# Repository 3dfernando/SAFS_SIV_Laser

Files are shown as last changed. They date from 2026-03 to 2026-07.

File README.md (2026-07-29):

# FSIV - A high-speed Focusing Schlieren Velocimetry system

Big thanks to MazinLab for publishing their laser driver! It enabled us to build this project at a very low cost!

## Samples

Here's a couple samples of the images acquired with this light source:

| Shear Layer of a M=0.98 jet (dt=800 ns) | Boundary Layer of a M=0.91 plug nozzle (dt=800 ns) |
|---|---|
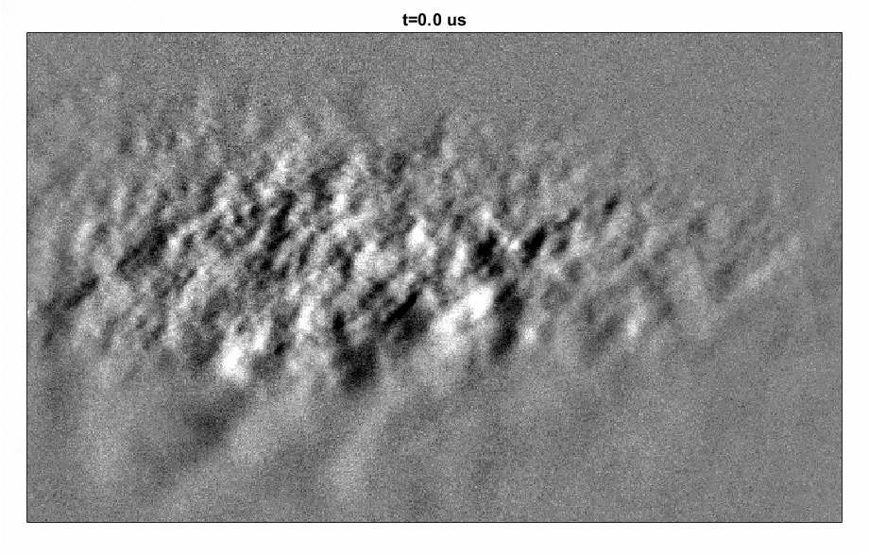
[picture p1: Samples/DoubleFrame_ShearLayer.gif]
Shear Layer
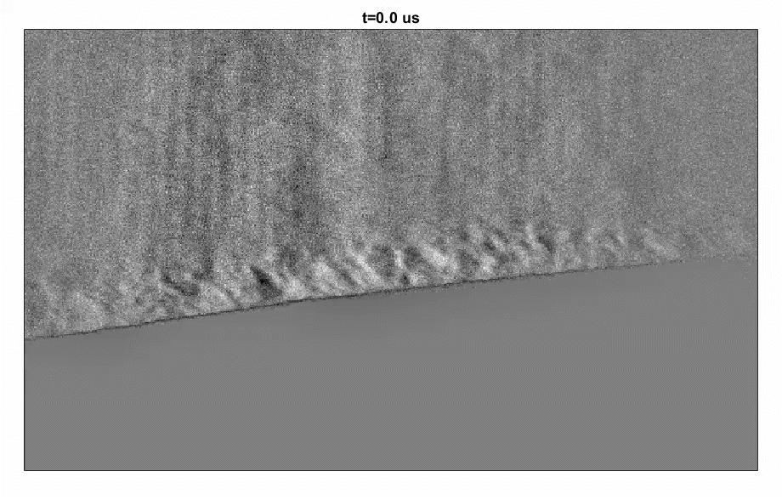
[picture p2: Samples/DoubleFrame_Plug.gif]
Boundary Layer
|  |  |

## Project Description

Velocimetry in high-speed aerodynamics (supersonic flows, more specifically) is very challenging. The flow velocities are so high that you need a high-frequency light source to be able to capture all the dynamics of the flow. More challengingly, the high velocities also bring the required delay between consecutive frames to order <500ns, requiring two light sources and the staggering of pulses.

For Particle Image Velocimetry (PIV), the laser must deliver sufficient pulse energy to scatter enough light onto the camera sensor — typically ≥10 mJ/pulse. Combined with the high-speed requirement, a suitable light source can exceed $200,000 USD, making this research prohibitively expensive even for well-funded laboratories. However, for schlieren imaging the amount of light required is much lower - about 10nJ/pulse are sufficient to fully illuminate the camera sensor and overcome the light losses. Thus, we developed a light source capable of ~400nJ/pulse and 30ns pulse width, which is adequate for most schlieren needs. 

Convective velocity — the velocity of turbulent structures and a key contributor to noise sources in aeroacoustics — requires at least two consecutive PIV velocity field measurements to be estimated from velocity data. However, if the flow structure can be captured directly through focusing schlieren (which images density gradients in the flow), it is possible to measure convective velocity directly by cross-correlating consecutive schlieren images.

Further, the double-pulsed schlieren images can also be processed with Online Dynamic Mode Decomposition (ODMD) to extract the coherent behavior of the flow at very high frequencies, limited by the Nyquist frequency based on the inter-frame pulse delay dt (typically <300 ns). For example, at dt=300 ns, this enables the observation of coherent structures up to ~1.7 MHz — beyond the capability of state-of-the-art high-speed cameras — at full camera resolution.

With our SAFS-SIV system, we are able to build a light source for under USD 1,000 capable of 50 kHz double-pulses with a 30 ns pulse width. At supersonic speeds, a 30 ns pulse corresponds to only ~2 μm of particle displacement, nearly eliminating motion blur. This low-cost device opens the door to high-speed flow diagnostics for a much broader range of research groups and institutions.

## Driver Picture

Below a photograph of our laser drivers forming a double-pulse system in a 1.0 mm fiber optic:

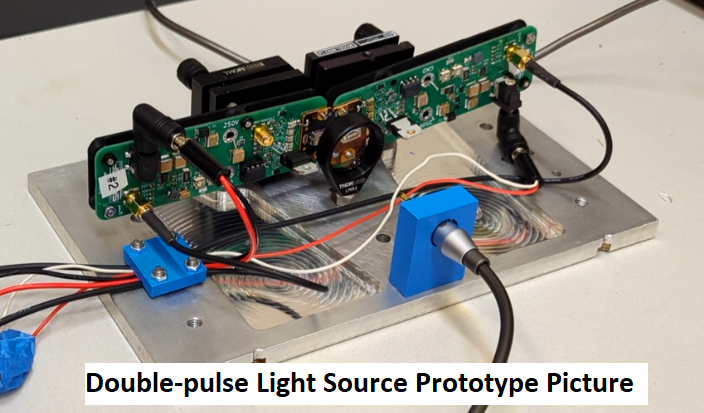
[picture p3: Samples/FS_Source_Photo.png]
Fiber source laser photo


A closer view of the PCB design:

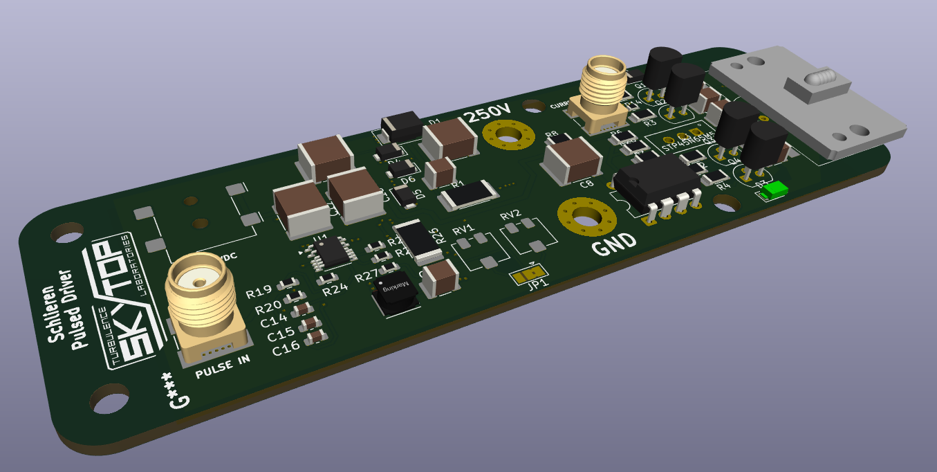
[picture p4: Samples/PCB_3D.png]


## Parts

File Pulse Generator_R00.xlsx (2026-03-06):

Description | Qty | Price/ea | Price total | Link
C2,C3,C4,C5,C6,C7 - 47p | 6 | $1.77 | $10.62 | https://www.digikey.com/en/products/detail/vishay-vitramon/VJ1210A470JXGAT5Z/1559967
SMA Connector | 3 | $6.95 | $20.85 | https://www.digikey.com/en/products/detail/amphenol-rf/132134-10/3125418
SMA/BNC Cable | 2 | $15.48 | $30.96 | https://www.digikey.com/en/products/detail/crystek-corporation/CCBNS-MM-RG174-18/1964572
C8,C12,C19 - 100n | 3 | $0.71 | $2.13 | https://www.digikey.com/en/products/detail/tdk-corporation/C4532X7R2J104K230KA/789694?s=N4IgTCBcDaICxwKwFowGYAMHkEZkDkARAHQBcQBdAXyA
C10,C18 - 1u | 2 | $2.85 | $5.70 | https://www.digikey.com/en/products/detail/kyocera-avx/2220CC105KAZ2A/11568650
C11,C16 - 1u | 2 | $0.08 | $0.16 | https://www.digikey.com/en/products/detail/samsung-electro-mechanics/CL10B105KP8NNNC/3887604?s=N4IgTCBcDaIIxgOwDYC0cCcAWNdUDkARAHQBcQBdAXyA
C15,C24 - 1n | 2 | $0.08 | $0.16 | https://www.digikey.com/en/products/detail/kemet/C0603C102K5RACTU/411081
C20,C21 - 220n | 2 | $1.00 | $2.00 | https://www.digikey.com/en/products/detail/murata-electronics/GRM55DR72J224KW01L/789368?s=N4IgTCBcDaICwE4AMBaAzAVjKgjCgcgCIA6ALiALoC%2BQA
C22,C23 - 2.2u | 2 | $0.18 | $0.36 | https://www.digikey.com/en/products/detail/murata-electronics/GRM188Z71E225ME43D/13905077
C1 - 10n | 1 | $0.38 | $0.38 | https://www.digikey.com/en/products/detail/johanson-dielectrics-inc/VPDF102W103K1GV001E/1557829
C14 - 220n | 1 | $0.15 | $0.15 | https://www.digikey.com/en/products/detail/murata-electronics/GCM188R71H224KA64D/2123158?s=N4IgTCBcDaICwE4AMBaArHJYUEYUDkARAHQBcQBdAXyA
C17 - 10u | 1 | $1.89 | $1.89 | https://www.digikey.com/en/products/detail/kyocera-avx/22201C106MAT2A/5431507
R2, R3, R4, R5, R6, R7 - 0Ohm | 6 | $0.10 | $0.60 | https://www.digikey.com/en/products/detail/stackpole-electronics-inc/RMCF1210ZT0R00/1715043
R8, R9, R10, R11, R12, R13 -0.5Ohm | 6 | $0.39 | $2.34 | https://www.digikey.com/en/products/detail/yageo/RL1210FR-070R5L/2827687
R14, R15, R19 - 50Ohm | 3 | $1.58 | $4.74 | https://www.digikey.com/en/products/detail/vishay-dale-thin-film/FC0603E50R0BTBST1/1769753
R18, R20 - 10k | 2 | $0.10 | $0.20 | https://www.digikey.com/en/products/detail/stackpole-electronics-inc/RMCF0603JT10K0/1758104
R1 - 1.2k | 1 | $0.15 | $0.15 | https://www.digikey.com/en/products/detail/koa-speer-electronics-inc/RK73B2ETTD122J/10314990
R16 - 4.7k | 1 | $0.10 | $0.10 | https://www.digikey.com/en/products/detail/yageo/RC0603FR-074K7L/727212
R21 - 18.2k | 1 | $0.10 | $0.10 | https://www.digikey.com/en/products/detail/stackpole-electronics-inc/RMCF0603FT18K2/1761004
R22 - 6.04k | 1 | $0.10 | $0.10 | https://www.digikey.com/en/products/detail/koa-speer-electronics-inc/RK73H1JTTD6041F/9844956
R23 - 107k | 1 | $0.10 | $0.10 | https://www.digikey.com/en/products/detail/yageo/RC0603FR-07107KL/726895
R24 - 84.5k | 1 | $0.10 | $0.10 | https://www.digikey.com/en/products/detail/yageo/RC0603FR-0784K5L/727408
R25 - 1M | 1 | $0.11 | $0.11 | https://www.digikey.com/en/products/detail/koa-speer-electronics-inc/RN73H1JTTD1004B25/10675094
R26 - 20Ohm | 1 | $0.10 | $0.10 | https://www.digikey.com/en/products/detail/stackpole-electronics-inc/RNCF0805DTE20R0/1708199
L1 - 10u | 1 | $2.35 | $2.35 | https://www.digikey.com/en/products/detail/w%C3%BCrth-elektronik/74437324100/2791051?s=N4IgTCBcDaIOwGYwFoFoGzIIzIHIBEAdAFxAF0BfIA
D2, D3, D4, D5, D6 - DFLS1150 | 5 | $0.38 | $1.90 | https://www.digikey.com/en/products/detail/diodes-incorporated/DFLS1150Q-7/6110470
D1 - S3MB-13F | 1 | $0.40 | $0.40 | https://www.digikey.com/en/products/detail/diodes-incorporated/S3MB-13-F/755456
U1 - LT8365 | 1 | $7.69 | $7.69 | https://www.digikey.com/en/products/detail/analog-devices-inc/LT8365EMSE-TRPBF/11586903
U2 - ISO6740 | 1 | $2.55 | $2.55 | https://www.digikey.com/en/products/detail/texas-instruments/ISO6740QDWRQ1/15205178
U3 - ADP7142ARDZ-5.0 | 1 | $4.89 | $4.89 | https://www.digikey.com/en/products/detail/analog-devices-inc/ADP7142ARDZ-5-0/6566216
U4 - LR8K4-G | 1 | $1.26 | $1.26 | https://www.digikey.com/en/products/detail/microchip-technology/LR8K4-G/4902849
RV1 - 50k | 1 | $1.58 | $1.58 | https://www.digikey.com/en/products/detail/bourns-inc/3314J-1-503E/86658
RV1 - 10k | 1 | $1.58 | $1.58 | https://www.digikey.com/en/products/detail/bourns-inc/3314J-1-103E/86580
J2 - Jack 2.0x5.5mm | 1 | $1.80 | $1.80 | https://www.digikey.com/en/products/detail/w%C3%BCrth-elektronik/694106106102/5047822?s=N4IgTCBcDaIOwGYwFoCsBOM7kEZkDkARAHQBcQBdAXyA
PLPT5 447KA Diode | 1 | $29.07 | $29.07 | https://www.digikey.com/en/products/detail/ams-osram-usa-inc/PLPT5-447KA/13541196
Nichita NUBM44 | 1 | $84.95 | $84.95 | https://www.amazon.com/Nichia-NUBM44-NUBM47-450nm-Laser/dp/B07662NHZZ
Diode Housing | 1 | $7.88 | $7.88 | https://www.amazon.com/12x30mm-9-0mm-Laser-Housing-200-1100nm/dp/B01G6GMIEM
Grand Total |  |  | $232.00

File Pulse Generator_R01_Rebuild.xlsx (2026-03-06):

Description | Qty | Price/ea | Price total | Link
C2,C3,C4,C5,C6,C7 - 47p | 6 | $1.77 | $10.62 | https://www.digikey.com/en/products/detail/vishay-vitramon/VJ1210A470JXGAT5Z/1559967
IC1 - UCC24742p | 10 | $1.62 | $16.20 | https://www.digikey.com/en/products/detail/texas-instruments/UCC27424P/603254?s=N4IgTCBcDaIKoGEFgOwBYxoAogLoF8g
Q5 - STP45N65M5 | 4 | $8.53 | $34.12 | https://www.digikey.com/en/products/detail/stmicroelectronics/STP45N65M5/3088028?s=N4IgTCBcDaIMoBUAKAWArAOQGxoLJpAF0BfIA
C16 - 1u | 2 | $0.08 | $0.16 | https://www.digikey.com/en/products/detail/samsung-electro-mechanics/CL10B105KP8NNNC/3887604?s=N4IgTCBcDaIIxgOwDYC0cCcAWNdUDkARAHQBcQBdAXyA
R25 - 1M | 2 | $0.11 | $0.22 | https://www.digikey.com/en/products/detail/koa-speer-electronics-inc/RN73H1JTTD1004B25/10675094
R24 - 84.5k | 2 | $0.10 | $0.20 | https://www.digikey.com/en/products/detail/yageo/RC0603FR-0784K5L/727408
R27 - 5.1k | 2 | $0.10 | $0.20 | https://www.digikey.com/en/products/detail/stackpole-electronics-inc/RMCF0603FT5K10/1760908
R23 - 107k | 2 | $0.10 | $0.20 | https://www.digikey.com/en/products/detail/yageo/RC0603FR-07107KL/726895
RV1 - 50k | 2 | $1.58 | $3.16 | https://www.digikey.com/en/products/detail/bourns-inc/3314J-1-503E/86658
RV1 - 10k | 2 | $1.58 | $3.16 | https://www.digikey.com/en/products/detail/bourns-inc/3314J-1-103E/86580
C15 - 1n | 2 | $0.08 | $0.16 | https://www.digikey.com/en/products/detail/kemet/C0603C102K5RACTU/411081
C19 - 100n | 2 | $0.71 | $1.42 | https://www.digikey.com/en/products/detail/tdk-corporation/C4532X7R2J104K230KA/789694?s=N4IgTCBcDaICxwKwFowGYAMHkEZkDkARAHQBcQBdAXyA
C18 - 1u | 2 | $2.85 | $5.70 | https://www.digikey.com/en/products/detail/kyocera-avx/2220CC105KAZ2A/11568650
C8, C17 - 10u | 4 | $1.89 | $7.56 | https://www.digikey.com/en/products/detail/kyocera-avx/22201C106MAT2A/5431507
C20,C21 - 220n | 4 | $1.00 | $4.00 | https://www.digikey.com/en/products/detail/murata-electronics/GRM55DR72J224KW01L/789368?s=N4IgTCBcDaICwE4AMBaAzAVjKgjCgcgCIA6ALiALoC%2BQA
C14 - 220n | 2 | $0.15 | $0.30 | https://www.digikey.com/en/products/detail/murata-electronics/GCM188R71H224KA64D/2123158?s=N4IgTCBcDaICwE4AMBaArHJYUEYUDkARAHQBcQBdAXyA
LD1 - NUBB-45 | 2 | $129.00 | $258.00 | https://lasertree.com/products/nichia-nubb45-455nm-34w-blue-laser-diode
C1 - 10n | 2 | $0.38 | $0.76 | https://www.digikey.com/en/products/detail/johanson-dielectrics-inc/VPDF102W103K1GV001E/1557829
L1 - 10u | 2 | $2.35 | $4.70 | https://www.digikey.com/en/products/detail/w%C3%BCrth-elektronik/74437324100/2791051?s=N4IgTCBcDaIOwGYwFoFoGzIIzIHIBEAdAFxAF0BfIA
R14, R19 - 50 Ohm | 2 | $1.58 | $3.16 | https://www.digikey.com/en/products/detail/vishay-dale-thin-film/FC0603E50R0BTBST1/1769753
D2, D3, D4, D5, D6 - DFLS1150 | 10 | $0.38 | $3.80 | https://www.digikey.com/en/products/detail/diodes-incorporated/DFLS1150Q-7/6110470
R5, R6, R7, R28- 4.7 Ohm | 8 | $0.10 | $0.80 | https://www.digikey.com/en/products/detail/stackpole-electronics-inc/RMCF1206FT4R70/1759916
R1 - 1.2k | 2 | $0.76 | $1.52 | https://www.digikey.com/en/products/detail/te-connectivity-passive-product/35221K2JT/5245016
R26 - 20 Ohm | 2 | $1.14 | $2.28 | https://www.digikey.com/en/products/detail/te-connectivity-passive-product/352220RFT/5245035
R8 - 470 Ohm | 2 | $0.10 | $0.20 | https://www.digikey.com/en/products/detail/yageo/RC1210FR-07470RL/5919610
R2, R3, R4, R12 - 0.4 Ohm | 8 | $0.15 | $1.20 | https://www.digikey.com/en/products/detail/yageo/RL1206JR-070R4L/5925149
R20 - 10k | 2 | $0.10 | $0.20 | https://www.digikey.com/en/products/detail/stackpole-electronics-inc/RMCF0603JT10K0/1758104
D1 - S3MB-13F | 2 | $0.40 | $0.80 | https://www.digikey.com/en/products/detail/diodes-incorporated/S3MB-13-F/755456
Q1, Q2, Q3, Q4 - ZTX415 | 10 | $13.60 | $136.00 | https://www.digikey.com/en/products/detail/diodes-incorporated/ZTX415/190185?s=N4IgTCBcDaIFoBUAaAWAjAVgLQDkAiIAugL5A
1mm Multimode Fiber POF Patch Cords , 2.0m | 1 | $33.57 | $33.57 | https://i-fiberoptics.com/patchcord-detail.php?summaryrow=12&series=181L&stock_number=IF%20181L-2-0
Grand Total |  |  | $534.37

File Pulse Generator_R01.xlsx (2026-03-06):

Description | Qty | Price/ea | Price total | Link
C2,C3,C4,C5,C6,C7 - 47p | 6 | $1.77 | $10.62 | https://www.digikey.com/en/products/detail/vishay-vitramon/VJ1210A470JXGAT5Z/1559967
SMA Connector | 2 | $6.95 | $13.90 | https://www.digikey.com/en/products/detail/amphenol-rf/132134-10/3125418
SMA/BNC Cable | 2 | $15.48 | $30.96 | https://www.digikey.com/en/products/detail/crystek-corporation/CCBNS-MM-RG174-18/1964572
IC1 - UCC24742p | 1 | $1.62 | $1.62 | https://www.digikey.com/en/products/detail/texas-instruments/UCC27424P/603254?s=N4IgTCBcDaIKoGEFgOwBYxoAogLoF8g
Q5 - STP45N65M5 | 1 | $8.53 | $8.53 | https://www.digikey.com/en/products/detail/stmicroelectronics/STP45N65M5/3088028?s=N4IgTCBcDaIMoBUAKAWArAOQGxoLJpAF0BfIA
C16 - 1u | 1 | $0.08 | $0.08 | https://www.digikey.com/en/products/detail/samsung-electro-mechanics/CL10B105KP8NNNC/3887604?s=N4IgTCBcDaIIxgOwDYC0cCcAWNdUDkARAHQBcQBdAXyA
R25 - 1M | 1 | $0.11 | $0.11 | https://www.digikey.com/en/products/detail/koa-speer-electronics-inc/RN73H1JTTD1004B25/10675094
R24 - 84.5k | 1 | $0.10 | $0.10 | https://www.digikey.com/en/products/detail/yageo/RC0603FR-0784K5L/727408
R27 - 5.1k | 1 | $0.10 | $0.10 | https://www.digikey.com/en/products/detail/stackpole-electronics-inc/RMCF0603FT5K10/1760908
R23 - 107k | 1 | $0.10 | $0.10 | https://www.digikey.com/en/products/detail/yageo/RC0603FR-07107KL/726895
RV1 - 50k | 1 | $1.58 | $1.58 | https://www.digikey.com/en/products/detail/bourns-inc/3314J-1-503E/86658
RV1 - 10k | 1 | $1.58 | $1.58 | https://www.digikey.com/en/products/detail/bourns-inc/3314J-1-103E/86580
C15 - 1n | 1 | $0.08 | $0.08 | https://www.digikey.com/en/products/detail/kemet/C0603C102K5RACTU/411081
C19 - 100n | 1 | $0.71 | $0.71 | https://www.digikey.com/en/products/detail/tdk-corporation/C4532X7R2J104K230KA/789694?s=N4IgTCBcDaICxwKwFowGYAMHkEZkDkARAHQBcQBdAXyA
C18 - 1u | 1 | $2.85 | $2.85 | https://www.digikey.com/en/products/detail/kyocera-avx/2220CC105KAZ2A/11568650
C8, C17 - 10u | 2 | $1.89 | $3.78 | https://www.digikey.com/en/products/detail/kyocera-avx/22201C106MAT2A/5431507
C20,C21 - 220n | 2 | $1.00 | $2.00 | https://www.digikey.com/en/products/detail/murata-electronics/GRM55DR72J224KW01L/789368?s=N4IgTCBcDaICwE4AMBaAzAVjKgjCgcgCIA6ALiALoC%2BQA
C14 - 220n | 1 | $0.15 | $0.15 | https://www.digikey.com/en/products/detail/murata-electronics/GCM188R71H224KA64D/2123158?s=N4IgTCBcDaICwE4AMBaArHJYUEYUDkARAHQBcQBdAXyA
U1 - LT8365 | 1 | $7.69 | $7.69 | https://www.digikey.com/en/products/detail/analog-devices-inc/LT8365EMSE-TRPBF/11586903
LD1 - NUBM-44 | 1 | $24.95 | $24.95 | https://barnettunlimited.com/product/nubm44u/
C1 - 10n | 1 | $0.38 | $0.38 | https://www.digikey.com/en/products/detail/johanson-dielectrics-inc/VPDF102W103K1GV001E/1557829
L1 - 10u | 1 | $2.35 | $2.35 | https://www.digikey.com/en/products/detail/w%C3%BCrth-elektronik/74437324100/2791051?s=N4IgTCBcDaIOwGYwFoFoGzIIzIHIBEAdAFxAF0BfIA
J2 - Jack 2.0x5.5mm | 1 | $1.80 | $1.80 | https://www.digikey.com/en/products/detail/w%C3%BCrth-elektronik/694106106102/5047822?s=N4IgTCBcDaIOwGYwFoCsBOM7kEZkDkARAHQBcQBdAXyA
R14, R19 - 50 Ohm | 2 | $1.58 | $3.16 | https://www.digikey.com/en/products/detail/vishay-dale-thin-film/FC0603E50R0BTBST1/1769753
D2, D3, D4, D5, D6 - DFLS1150 | 5 | $0.38 | $1.90 | https://www.digikey.com/en/products/detail/diodes-incorporated/DFLS1150Q-7/6110470
R5, R6, R7, R28- 4.7 Ohm | 4 | $0.10 | $0.40 | https://www.digikey.com/en/products/detail/stackpole-electronics-inc/RMCF1206FT4R70/1759916
R1 - 1.2k | 1 | $0.76 | $0.76 | https://www.digikey.com/en/products/detail/te-connectivity-passive-product/35221K2JT/5245016
R26 - 20 Ohm | 1 | $1.14 | $1.14 | https://www.digikey.com/en/products/detail/te-connectivity-passive-product/352220RFT/5245035
R8 - 470 Ohm | 1 | $0.10 | $0.10 | https://www.digikey.com/en/products/detail/yageo/RC1210FR-07470RL/5919610
R2, R3, R4, R12 - 0.4 Ohm | 4 | $0.15 | $0.60 | https://www.digikey.com/en/products/detail/yageo/RL1206JR-070R4L/5925149
R20 - 10k | 1 | $0.10 | $0.10 | https://www.digikey.com/en/products/detail/stackpole-electronics-inc/RMCF0603JT10K0/1758104
D1 - S3MB-13F | 1 | $0.40 | $0.40 | https://www.digikey.com/en/products/detail/diodes-incorporated/S3MB-13-F/755456
Q1, Q2, Q3, Q4 - ZTX415 | 4 | $13.60 | $54.40 | https://www.digikey.com/en/products/detail/diodes-incorporated/ZTX415/190185?s=N4IgTCBcDaIFoBUAaAWAjAVgLQDkAiIAugL5A
Grand Total |  |  | $178.98

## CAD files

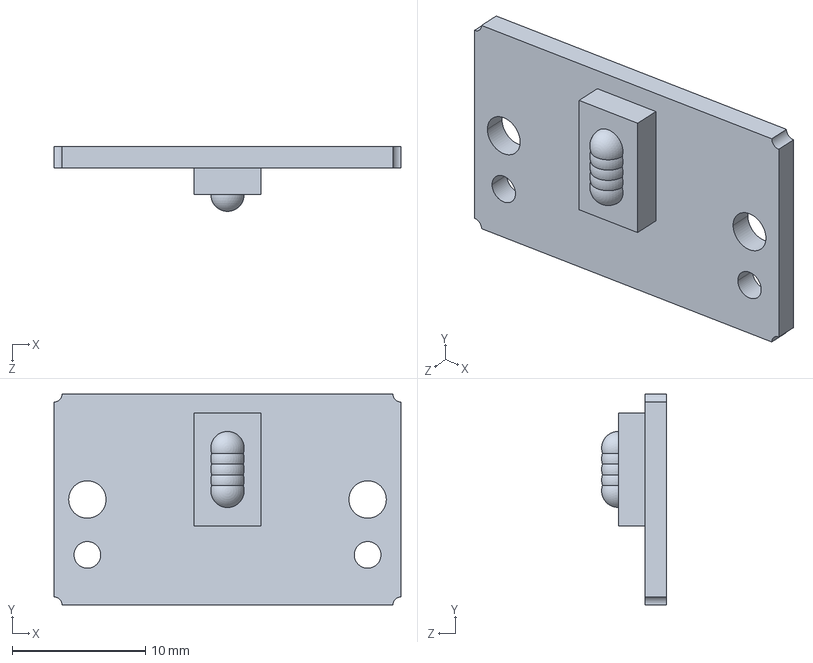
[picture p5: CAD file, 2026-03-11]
Laser_Driver/NUBB-45.STEP
26.0 x 15.8 x 4.86 mm

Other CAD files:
Laser_Driver/NUBB-45.SLDPRT

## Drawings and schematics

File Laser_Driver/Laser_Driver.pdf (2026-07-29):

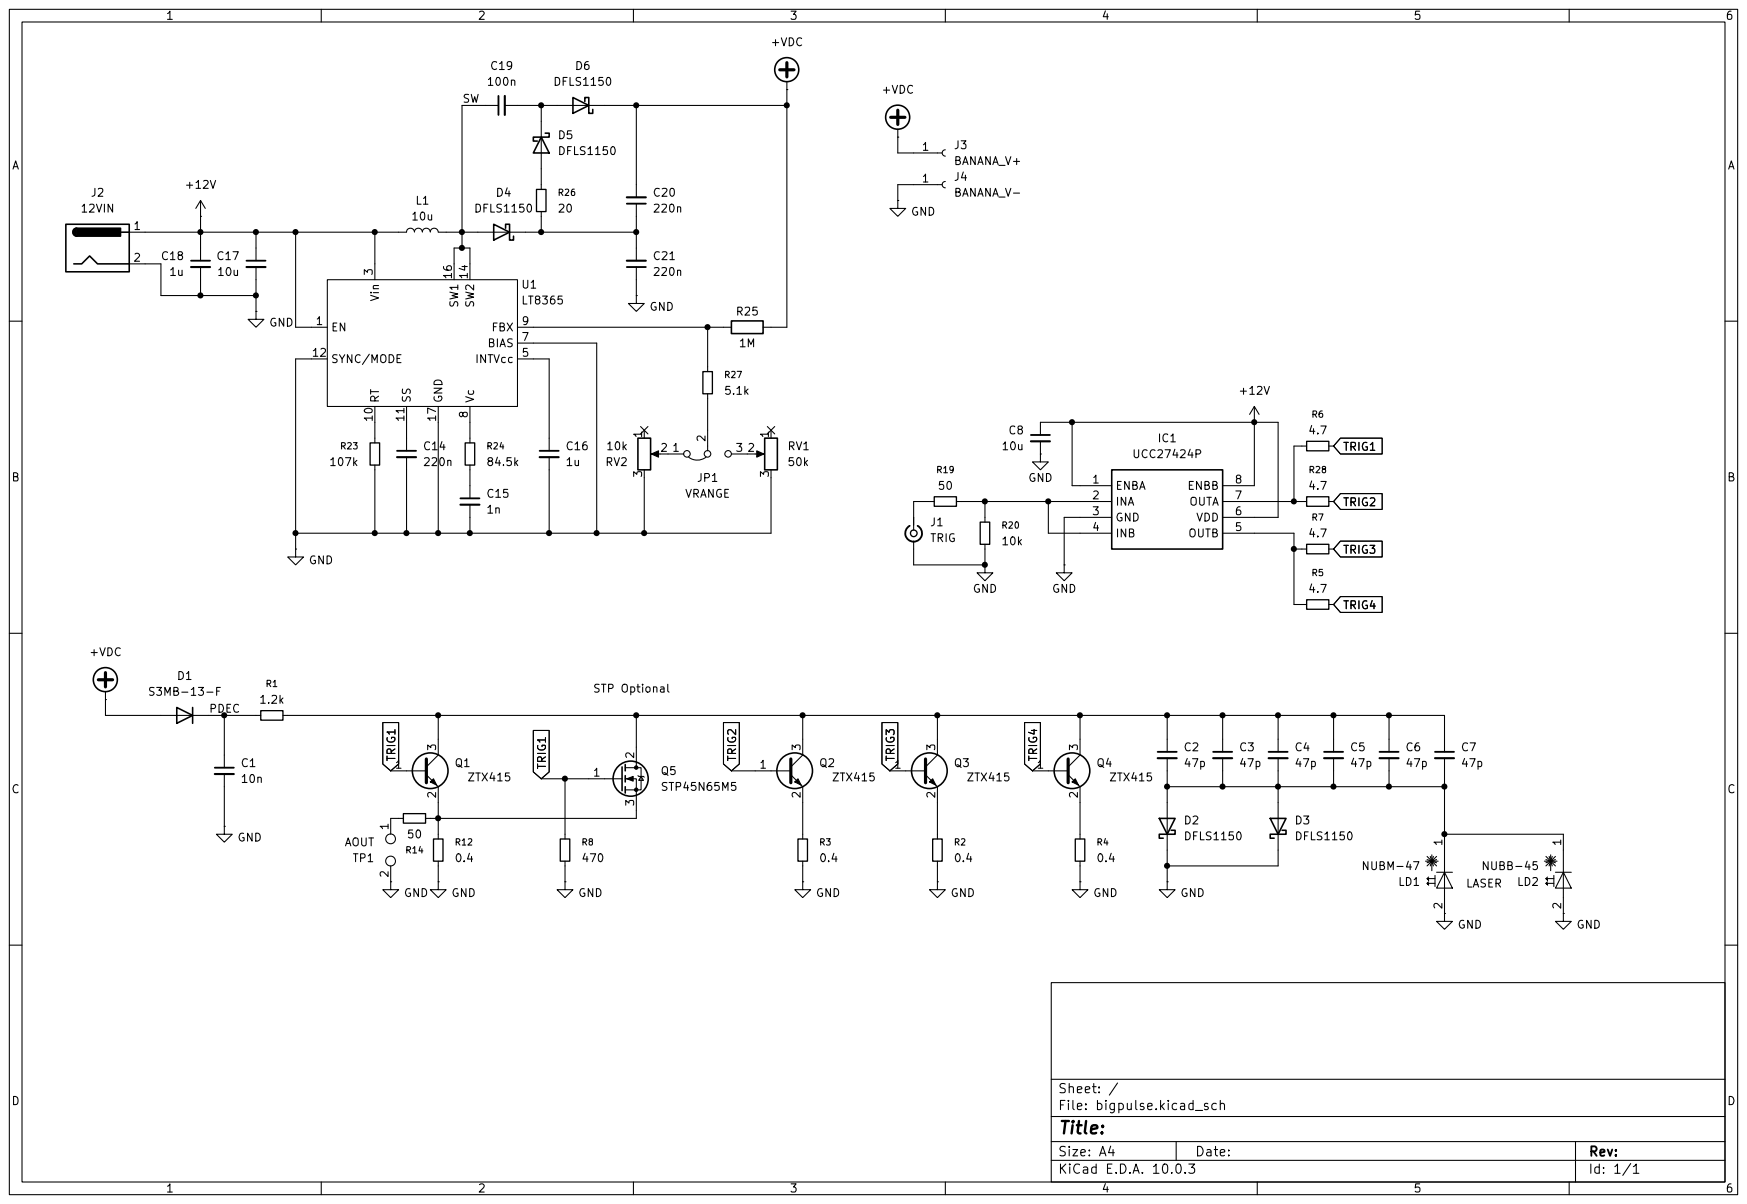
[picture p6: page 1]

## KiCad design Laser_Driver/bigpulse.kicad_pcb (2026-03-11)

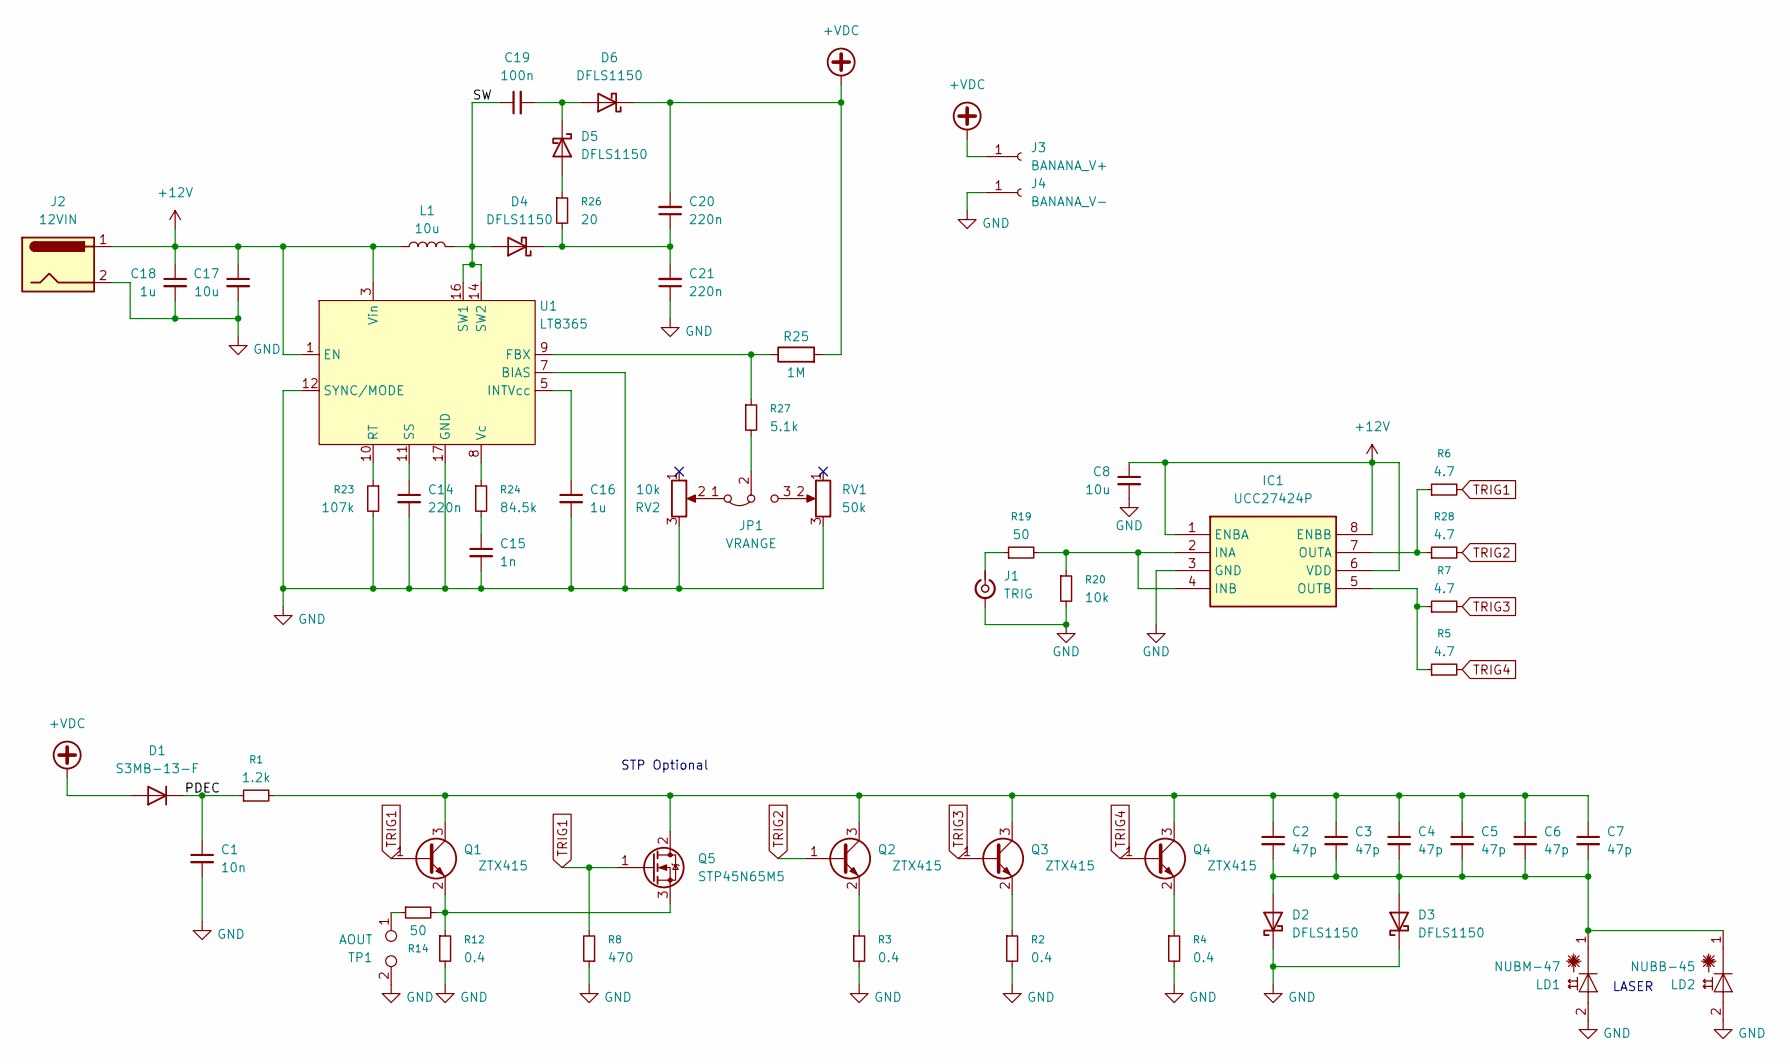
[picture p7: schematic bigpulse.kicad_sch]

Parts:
C1: 10n; C_1210_3225Metric; DIGIKEY_PN 709-VPDF102W103K1GV001ECT-ND
C2, C3, C4, C5, C6, C7: 47p; C_1210_3225Metric; DIGIKEY_PN 720-1040-1-ND
C8, C17: 10u; C_2220_5750Metric; DIGIKEY_PN 478-KGM55DR72A106MVCT-ND
C14: 220n; C_0603_1608Metric; DIGIKEY_PN 490-5402-1-ND
C15: 1n; C_0603_1608Metric; DIGIKEY_PN 399-C0603C102K5RACTUCT-ND
C16: 1u; C_0603_1608Metric; DIGIKEY_PN 1276-1946-1-ND
C18: 1u; C_2220_5750Metric; DIGIKEY_PN 478-KGF55DR72J105KVCT-ND
C19: 100n; C_1210_3225Metric; DIGIKEY_PN 445-2300-1-ND
C20, C21: 220n; C_2220_5750Metric; DIGIKEY_PN 490-3520-1-ND
D1: S3MB-13-F; D_SMB; DIGIKEY_PN S3MB-FDICT-ND
D2, D3, D4, D5, D6: DFLS1150; D_PowerDI-123; DIGIKEY_PN DFLS1150Q-7DICT-ND
IC1: UCC27424P; DIP-8_W7.62mm; Mouser Part Number 595-UCC27424P
J1: TRIG; SMA_Amphenol_132134-10_Vertical; DIGIKEY_PN 132134-10
J2: 12VIN; BarrelJack_Wuerth_694106106102_2.0x5.5mm; DIGIKEY_PN 732-5929-1-ND
J3: BANANA_V+; MountingHole_3.7mm_Pad_Via; DIGIKEY_PN J10125-ND
J4: BANANA_V-; MountingHole_3.7mm_Pad_Via; DIGIKEY_PN J10126-ND
JP1: VRANGE; SolderJumper-3_P1.3mm_Bridged2Bar12_Pad1.0x1.5mm
L1: 10u; L_Wurth_WE-LQSH-4020; DIGIKEY_PN 732-3336-1-ND
LD1: NUBM-47; NUBM44
LD2: NUBB-45; NUBB45
Q1, Q2, Q3, Q4: ZTX415; TO-92; DIGIKEY_PN ZTX415-ND
Q5: STP45N65M5
R1: 1.2k; R_2512_6332Metric_Pad1.40x3.35mm_HandSolder
R2, R3, R4, R12: 0.4; R_1206_3216Metric_Pad1.30x1.75mm_HandSolder
R5, R6, R7, R28: 4.7; R_1206_3216Metric_Pad1.30x1.75mm_HandSolder
R8: 470; R_1210_3225Metric
R14, R19: 50; R_0603_1608Metric; DIGIKEY_PN 764-FC0603E50R0BTBST1CT-ND
R20: 10k; R_0603_1608Metric; DIGIKEY_PN RMCF0603JT10K0CT-ND
R23: 107k; R_0603_1608Metric; DIGIKEY_PN 311-107KHRCT-ND
R24: 84.5k; R_0603_1608Metric; DIGIKEY_PN 311-84.5KHRCT-ND
R25: 1M; R_0603_1608Metric; DIGIKEY_PN 2019-RN73H1JTTD1004B25CT-ND
R26: 20; R_2512_6332Metric_Pad1.40x3.35mm_HandSolder
R27: 5.1k; R_0603_1608Metric
RV1: 50k; Potentiometer_Bourns_3314S_Horizontal; DIGIKEY_PN 3314J-503ECT-ND
RV2: 10k; Potentiometer_Bourns_3314S_Horizontal; DIGIKEY_PN 3314J-103ECT-ND
TP1: AOUT; SMA_Amphenol_132134-10_Vertical; DIGIKEY_PN 132134-10
U1: LT8365; Analog_MSOP-12-16-1EP_3x4.039mm_P0.5mm_EP1.651x2.845mm_Ther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; DIGIKEY_PN 505-LT8365EMSE#TRPBFCT-ND

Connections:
+12V: C8.1, C17.1, C18.1, IC1.1 (ENBA), IC1.6 (VDD), IC1.8 (ENBB), J2.1, L1.1, U1.1 (EN), U1.3 (Vin)
+VDC: C20.2, D1.2 (A), D6.1 (K), J3.1, R25.2
/PDEC: C1.1, D1.1 (K), R1.1
/SW: C19.1, D4.2 (A), L1.2, U1.14 (SW2), U1.16 (SW1)
GND: C1.2, C8.2, C14.2, C15.2, C16.2, C17.2, C18.2, C21.1, D2.1 (K), D3.1 (K), IC1.3 (GND), J1.2 (Ext), J2.2, J4.1, LD1.2 (A), LD2.2 (A), R2.2, R3.2, R4.2, R8.1, R12.2, R20.2, R23.2, RV1.3, RV2.3, TP1.2, U1.7 (BIAS), U1.12 (SYNC/MODE), U1.17 (GND)
unnamed: C15.1, R24.2
unnamed: C2.2, C3.2, C4.2, C5.2, C6.2, C7.2, D2.2 (A), D3.2 (A), LD1.1 (C), LD2.1 (C)
unnamed: C20.1, C21.2, D4.1 (K), R26.2
unnamed: D5.2 (A), R26.1
unnamed: C19.2, D5.1 (K), D6.2 (A)
unnamed: IC1.2 (INA), IC1.4 (INB), R19.2, R20.1
unnamed: IC1.7 (OUTA), R6.1, R28.1
unnamed: IC1.5 (OUTB), R5.1, R7.1
unnamed: J1.1 (In), R19.1
unnamed: JP1.1 (A), RV2.2
unnamed: JP1.3 (B), RV1.2
unnamed: JP1.2 (C), R27.2
unnamed: C2.1, C3.1, C4.1, C5.1, C6.1, C7.1, Q1.3 (C), Q2.3 (C), Q3.3 (C), Q4.3 (C), Q5.2 (D), R1.2
unnamed: Q1.2 (E), Q5.3 (S), R12.1, R14.2
unnamed: Q2.2 (E), R3.1
unnamed: Q3.2 (E), R2.1
unnamed: Q4.2 (E), R4.1
unnamed: R14.1, TP1.1
unnamed: R25.1, R27.1, U1.9 (FBX)
unnamed: C16.1, U1.5 (INTVcc)
unnamed: R23.1, U1.10 (RT)
unnamed: C14.1, U1.11 (SS)
unnamed: R24.1, U1.8 (Vc)
TRIG1: Q1.1 (B), Q5.1 (G), R6.2, R8.2
TRIG2: Q2.1 (B), R28.2
TRIG3: Q3.1 (B), R7.2
TRIG4: Q4.1 (B), R5.2

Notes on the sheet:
STP Optional
LASER

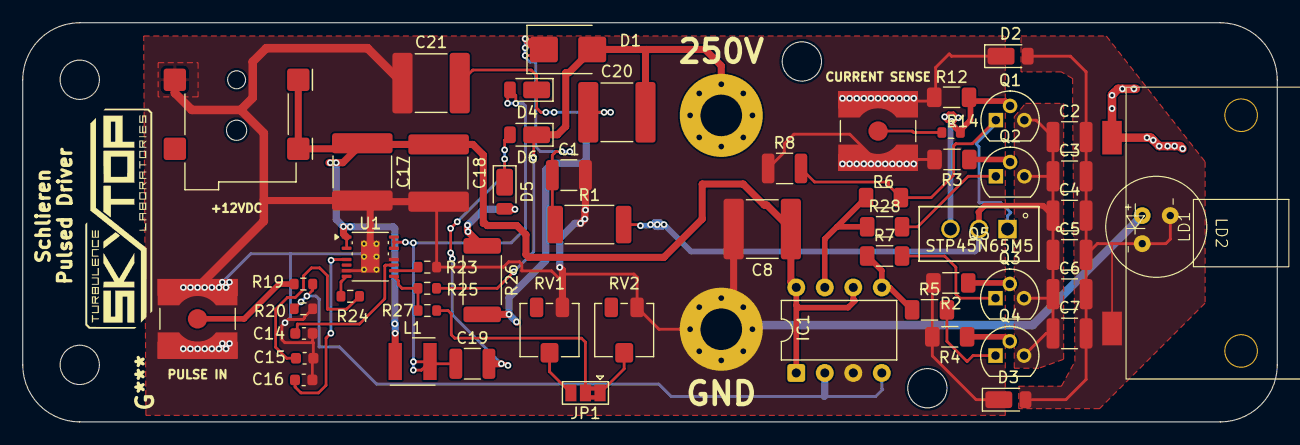
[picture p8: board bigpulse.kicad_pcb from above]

Board: 2 copper layers, 111.8 x 35.6 mm, 61 parts (0 on the bottom side), 32 nets.

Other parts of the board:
H**: 1/4 20; quarter-twenty
H**#2, H**#3: 1/4 20; quarter-twenty

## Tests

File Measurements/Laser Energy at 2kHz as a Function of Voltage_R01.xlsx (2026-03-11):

Voltage [V] | Pulse Frequency [Hz] | Cap Energy [uJ] | Optical Power [uW] | Energy / pulse [nJ] | Assumed Pulse Width [ns] | Peak Power [W] | Optical Efficiency
Laser 1 [Blue NUBM-44] (Test on 01/18/26)
180 | 2000 | 4.6 | 185 | 92.5 | 7 | 13.2 | 2.0%
190 | 2000 | 5.1 | 215 | 107.5 | 7 | 15.4 | 2.1%
202 | 2000 | 5.8 | 249 | 124.5 | 7 | 17.8 | 2.2%
214 | 2000 | 6.5 | 282 | 141 | 7 | 20.1 | 2.2%
227 | 2000 | 7.3 | 321 | 160.5 | 7 | 22.9 | 2.2%
237 | 2000 | 7.9 | 345 | 172.5 | 7 | 24.6 | 2.2%
255 | 2000 | 9.2 | 405 | 202.5 | 7 | 28.9 | 2.2%
Laser 2 [Blue NUBM-44] (Test on 01/18/26)
171 | 2000 | 4.1 | 220 | 110 | 7 | 15.7 | 2.7%
181 | 2000 | 4.6 | 288 | 144 | 7 | 20.6 | 3.1%
191 | 2000 | 5.1 | 331 | 165.5 | 7 | 23.6 | 3.2%
200.6 | 2000 | 5.7 | 376 | 188 | 7 | 26.9 | 3.3%
216 | 2000 | 6.6 | 436 | 218 | 7 | 31.1 | 3.3%
229 | 2000 | 7.4 | 489 | 244.5 | 7 | 34.9 | 3.3%
251 | 2000 | 8.9 | 574 | 287 | 7 | 41.0 | 3.2%
[Green Z-80 laser] (Test on 02/22/26)
164 | 1000 | 3.8 | 41.6 | 41.6 | 7 | 5.9 | 1.1%
169.5 | 1000 | 4.1 | 44.6 | 44.6 | 7 | 6.4 | 1.1%
181.3 | 1000 | 4.6 | 49.5 | 49.5 | 7 | 7.1 | 1.1%
191.3 | 1000 | 5.2 | 53.3 | 53.3 | 7 | 7.6 | 1.0%
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

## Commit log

2026-03-06 Option for NUBB45 and Improvements
    [NUBB-45.SLDPRT, NUBB-45.STEP, Pulse Generator_R00.xlsx, Pulse Generator_R00_2PC.xlsx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]
2026-03-11 Minor improvements after prototyping
    Legs of MOSFET were switched.
    [NUBB-45.SLDPRT, NUBB-45.STEP, bigpulse.kicad_pcb, bigpulse.kicad_sch]
2026-03-11 Energy Measurements with new board
    [Laser Energy at 2kHz as a Function of Voltage_R01.xlsx]
2026-06-04 Gif Samples of double-pulse focusing schlieren

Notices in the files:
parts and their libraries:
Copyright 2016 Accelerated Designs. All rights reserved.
